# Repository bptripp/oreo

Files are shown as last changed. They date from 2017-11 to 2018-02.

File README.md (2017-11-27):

# oreo

OREO is a 7-degree-of-freedom robotic head that is modelled on the primate visual system. It performs saccades at realistic human speeds. The eyes have a realistic range of motion, including vergence. It also supports rapid changes in focus distance.

Further documentation is in development. In the mean time please contact Bryan Tripp (bptripp@uwaterloo.ca) for more information. 

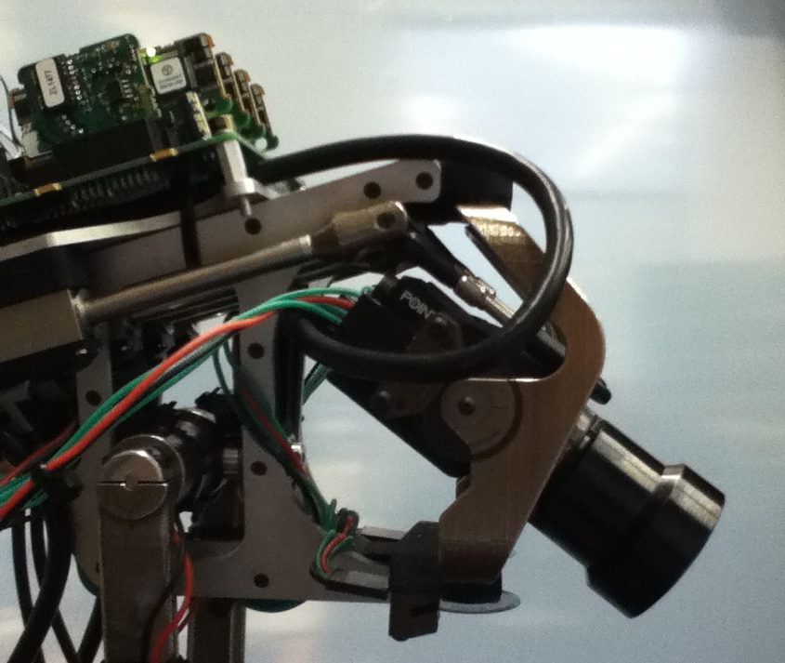
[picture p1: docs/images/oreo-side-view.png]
OREO photo


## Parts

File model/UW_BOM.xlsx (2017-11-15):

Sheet: Eye_Sub_ASM
PN | Description | Supplier | Material | Est. Cost (USD) 1 | Est. Cost (USD) 5 | Est. Cost (USD) 10 | QTY. / Package | QTY. Req'd | Order QTY. | Part Cost | CAD File name | Link
XXX | Lens Assembly | B-CON | Assembly | 0 | N/A | N/A | 1 | 1 | 1 | 0 | N/A | N/A
4262T5 | Ultra-Precision Mini Stainless Steel Ball Bearing - ABEC-7, Flanged Double Shielded for 3/32" Shaft Diameter, 5/16" OD | McMaster-Carr | 440C Stainless Steel | 12.76 | N/A | N/A | 1 | 3 | 3 | 38.28 | 4262T500.SLDPRT | http://www.mcmaster.com/#catalog/121/1183/=10p1i0g
90318A101 | Ultra Low Profile Type 316 Stainless Steel Shoulder Screw, Socket Drive, 3/32" Diameter X1/8" Long Shoulder, 2-56 Thread | McMaster-Carr | 316 Stainless Steel | 4.26 | 3.63 | N/A | 1 | 3 | 3 | 12.78 | 90318A101.SLDPRT | http://www.mcmaster.com/#90318a101/=10p1ko5
91294A002 | Class 10.9, M2 Size, 4mm Length, .4mm Pitch, Black Alloy Steel Flat-Head Socket Cap Screw | McMaster-Carr | Black-Oxide | 6.42 | N/A | N/A | 25 | 4 | 1 | 6.42 | 91294A002.SLDPRT | http://www.mcmaster.com/#91294a002/=10p1pz1
91239A758 | Class 10.9 Steel Button-Head Socket Cap Screw, M2.5 Size, 12 mm Length, .45 mm Pitch | McMaster-Carr | Black Oxide | 10.5 | N/A | N/A | 25 | 2 | 1 | 10.5 | 91239A758.SLDPRT | http://www.mcmaster.com/#91239a758/=10p1rd7
91255A075 | Alloy Steel Button-Head Socket Cap Screw, Black-Oxide, 2-56 Thread, 1/16" Long | McMaster-Carr | Black Oxide | 7.25 | N/A | N/A | 25 | 1 | 1 | 7.25 | 91255A075.SLDPRT | http://www.mcmaster.com/#91255a075/=10p1seu
9712K510 | High-Carbon Steel Belleville Disc Spring, .093" ID, .187" OD, .007" Thick | McMaster-Carr | High Carbon Steel | 12.03 | N/A | N/A | 12 | 1 | 1 | 12.03 | 9712K510.SLDPRT | http://www.mcmaster.com/#9712k51/=10p1tbr
99040A210 | Stainless Steel Shim for Shafts, 0.010" Thick, 0.093" ID, 0.203" OD | McMaster-Carr | 18-8 Stainless Steel | 11.29 | N/A | N/A | 25 | 2 | 1 | 11.29 | 99040A210.SLDPRT | http://www.mcmaster.com/#99040a210/=10p1zgw
91239A115 | Class 10.9 Steel Button-Head Socket Cap Screw, M3 Size, 10 mm Length, .5 mm Pitch | McMaster-Carr | Black Oxide | 6.88 | N/A | N/A | 100 | 2 | 1 | 6.88 | 91239A115.SLDPRT | http://www.mcmaster.com/#91239a115/=111uhff
FL3-U3-13S2M-CS | Camera, Flea3 | Point Grey | Assembly | 525 | N/A | N/A | 1 | 0 | 0 | 0 | FL2-006-R0.SLDPRT | https://www.ptgrey.com/flea3-13-mp-mono-usb3-vision-sony-imx035-camera
cam_mount_Al | Camera Mount Aluminum | ProtoLabs | 6061-T6 Aluminum | 468.14 | N/A | N/A | 1 | 0 | 0 | 0 | cam_mount.STEP | https://myaccount.protolabs.com
yoke_Al | Yoke Aluminum | ProtoLabs | 6061-T6 Aluminum | 1293.12 | N/A | N/A | 1 | 0 | 0 | 0 | yoke.STEP | https://myaccount.protolabs.com
cam_mount_SS | Camera Mount Stainless | Shapeways | Printed Stainless Steel | 48.14 | N/A | N/A | 1 | 0 | 0 | 0 | cam_mount.STL | https://www.shapeways.com
cam_mount_Ny | Camera Mount Plastic | Shapeways | Strong and Flexible Black | 13.46 | N/A | N/A | 1 | 0 | 0 | 0 | cam_mount.STL | https://www.shapeways.com
yoke_SS | Yoke Stainless | Shapeways | Printed Stainless Steel | 48.87 | N/A | N/A | 1 | 0 | 0 | 0 | yoke.STL | https://www.shapeways.com
yoke_Ny | Yoke Plastic | Shapeways | Strong and Flexible Black | 9.76 | N/A | N/A | 1 | 0 | 0 | 0 | yoke.STL | https://www.shapeways.com
EM2-1-5000-I | Encoder | US Digital | Plastic | 58.1 | 40.1 | 35.71 | 1 | 1 | 1 | 58.1 | EM1-X-X.SLDPRT | http://www.usdigital.com/products/encoders/incremental/modules/EM2
DISK-1-5000-093-IE | Encoder Disk | US Digital | Mylar | 13.63 | 9.42 | 8.11 | 1 | 2 | 2 | 27.26 | encoder_disk.SLDPRT | http://www.usdigital.com/products/encoders/incremental/rotary/disks/DISK-1
TOTAL |  |  |  |  |  |  |  |  |  | 190.79

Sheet: Frame_Sub_ASM
PN | Description | Supplier | Material | Est. Cost (USD) 1 | Est. Cost (USD) 5 | Est. Cost (USD) 10 | QTY. / Package | QTY. Req'd | Order QTY. | Part Cost | CAD File name | Link
B75AECFD27A3 | Motor | Maxon | Assembly | 318 | N/A | N/A | 1 | 1 | 1 | 318 | maxon_PN_B75AECFD27A3.sldasm | http://www.maxonmotorusa.com/maxon/view/configurator/?ConfigID=B75AECFD27A3
4262T5 | Ultra-Precision Mini Stainless Steel Ball Bearing - ABEC-7, Flanged Double Shielded for 3/32" Shaft Diameter, 5/16" OD | McMaster-Carr | 440C Stainless Steel | 12.76 | N/A | N/A | 1 | 4 | 4 | 51.04 | 4262T500.SLDPRT | http://www.mcmaster.com/#catalog/121/1183/=10p1i0g
90318A102 | Ultra Low Profile Type 316 Stainless Steel Shoulder Screw, Socket Drive, 3/32" Diameter X1/4" Long Shoulder, 2-56 Thread | McMaster-Carr | 316 Stainless Steel | 4.29 | 3.66 | N/A | 1 | 6 | 6 | 25.74 | 90318A102.SLDPRT | http://www.mcmaster.com/#90318a102/=10p2m1d
99040A210 | Stainless Steel Shim for Shafts, 0.010" Thick, 0.093" ID, 0.203" OD | McMaster-Carr | 18-8 Stainless Steel | 11.29 | N/A | N/A | 25 | 10 | 1 | 11.29 | 99040A210.SLDPRT | http://www.mcmaster.com/#99040a210/=10p1zgw
91239A758 | Class 10.9 Steel Button-Head Socket Cap Screw, M2.5 Size, 12 mm Length, .45 mm Pitch | McMaster-Carr | Black Oxide | 10.5 | N/A | N/A | 25 | 6 | 1 | 10.5 | 91239A758.SLDPRT | http://www.mcmaster.com/#91239a758/=10p1rd7
3088A119 | Steel Shim, Round, 0.001" Thick, 1/4" ID, 3/8" OD | McMaster-Carr | Steel | 5.22 | N/A | N/A | 10 | 4 | 1 | 5.22 | N/A | http://www.mcmaster.com/#3088a119/=10p39ua
3088A229 | Steel Shim, Round, 0.005" Thick, 1/4" ID, 3/8" OD | McMaster-Carr | Steel | 3.66 | N/A | N/A | 10 | 1 | 1 | 3.66 | N/A | http://www.mcmaster.com/#3088a229/=10p394m
4262T36 | Premium Flanged Ball Bearing, Double Shielded, Trade No.FR188-2Z | McMaster-Carr | 440C Stainless Steel | 10.47 | N/A | N/A | 1 | 3 | 3 | 31.41 | 4262T36.SLDPRT | http://www.mcmaster.com/#4262t36/=113ctkg
90337A197 | Low Profile 18-8 Stainless Steel Shoulder Screw, Socket Drive, 1/4" Diameter X5/8" Long Shoulder, 10-32 Thread | McMaster-Carr | 18-8 Stainless | 10.47 | 8.88 | N/A | 1 | 3 | 3 | 31.41 | 90337A197.SLDPRT | http://www.mcmaster.com/#90337a197/=10p3d4d
91294A005 | Black Alloy Steel Flat-Head Socket Cap Screw, Class 10.9, M2 Size, 8mm Length, .4mm Pitch | McMaster-Carr | Black Oxide | 6.45 | N/A | N/A | 25 | 30 | 2 | 12.9 | 91294A005.SLDPRT | http://www.mcmaster.com/#91294a005/=10p4dr9
91294A006 | Black Alloy Steel Flat-Head Socket Cap Screw, Class 10.9, M2 Size, 10mm Length, .4mm Pitch | McMaster-Carr | Black Oxide | 6.65 | N/A | N/A | 25 | 3 | 1 | 6.65 | 91294A006.SLDPRT | http://www.mcmaster.com/#91294a006/=10p4368
93657A005 | Metric Nylon Unthreaded Spacer 6mm OD, 4mm Length, M3 Screw Size | McMaster-Carr | Nylon | 1.06 | N/A | 0.89 | 1 | 8 | 8 | 8.48 | 93657A005.SLDPRT | http://www.mcmaster.com/#93657a005/=10qlcg0
91294A132 | Black Alloy Steel Flat-Head Socket Cap Screw, Class 10.9, M3 Size, 12mm Length, .50 Pitch | McMaster-Carr | Black Oxide | 5.38 | N/A | N/A | 100 | 4 | 1 | 5.38 | 91294A132.SLDPRT | http://www.mcmaster.com/#91294a132/=111u497
91292A265 | Type 18-8 Stainless Steel Socket Head Cap Screw, M1.6 Thread, 10mm Long, 0.35mm Pitch | McMaster-Carr | 18-8 Stainless | 9.78 | N/A | N/A | 50 | 16 | 1 | 9.78 | 91292A265.SLDPRT | http://www.mcmaster.com/#91292a265/=111u6c4
91239A115 | lass 10.9 Steel Button-Head Socket Cap Screw, M3 Size, 10 mm Length, .5 mm Pitc | McMaster-Carr | Black Oxide | 6.88 | N/A | N/A | 100 | 4 | 1 | 6.88 | 91239A115.SLDPRT | http://www.mcmaster.com/#91239a115/=111uhff
95893A550 | Thread-Forming Torx Screw for Plastics, Flat Head, 18-8 Stainless Steel, 2-28 Thread, 1/4" Length | McMaster-Carr | 18-8 Stainless | 12.24 | N/A | N/A | 50 | 30 | 1 | 12.24 | 95893A550.SLDPRT | http://www.mcmaster.com/#95893a550/=111u4qr
LM 1247–060–11 | Linear Actuator | MicroMo | Assembly | 539.3 | N/A | N/A | 1 | 6 | 6 | 3235.8 | LM1247-060-XX.SLDASM | http://www.micromo.com/products/linear-motors/quickshaft-data-sheets
Motor Mount Inside_AL | Motor Mount Inside | protolabs | 6061-T6 Aluminum | 291.5 | N/A | N/A | 1 | 0 | 0 | 0 | motor_mount_inside.STEP | https://myaccount.protolabs.com
Yaw Bottom Bearing Mount_AL | Yaw Bottom Bearing Mount | protolabs | 6061-T6 Aluminum | 187.81 | N/A | N/A | 1 | 0 | 0 | 0 | yaw_bearing_mount_bottom.STEP | https://myaccount.protolabs.com
Yaw Top Bearing Mount_AL | Yaw Top Bearing Mount | protolabs | 6061-T6 Aluminum | 175.12 | N/A | N/A | 1 | 0 | 0 | 0 | yaw_bearing_mount_top.STEP | https://myaccount.protolabs.com
Roll Motor Mount_AL | Roll Motor Mount | protolabs | 6061-T6 Aluminum | 189.09 | N/A | N/A | 1 | 0 | 0 | 0 | roll_motor_mount.STEP | https://myaccount.protolabs.com
Roll Bearing Mount_AL | Roll Bearing Mount | protolabs | 6061-T6 Aluminum | 429.5 | N/A | N/A | 1 | 0 | 0 | 0 | roll_bearing_mount.STEP | https://myaccount.protolabs.com
frame_plate_side_l | frame_plate_side_l | ProtoLabs | 7075-T651 Aluminum | 150.04 | 123.13 | 111.41 | 1 | 1 | 1 | 150.04 | frame_plate_side_l.STEP | https://myaccount.protolabs.com
frame_plate_side_r | frame_plate_side_r | ProtoLabs | 7075-T651 Aluminum | 150.04 | 123.13 | 111.41 | 1 | 1 | 1 | 150.04 | frame_plate_side_r.STEP | https://myaccount.protolabs.com
frame_plate_top | frame_plate_top | ProtoLabs | 7075-T651 Aluminum | 160.02 | 133.1 | 121.38 | 1 | 1 | 1 | 160.02 | frame_plate_top.STEP | https://myaccount.protolabs.com
Motor Mount Inside_SS | Motor Mount Inside | Shapeways | Printed Stainless Steel | 51.92 | N/A | N/A | 1 | 0 | 0 | 0 | motor_mount_inside.STL | https://www.shapeways.com
Motor Mount Inside_NY | Motor Mount Inside | Shapeways | Strong and Flexible Black | 8.88 | N/A | N/A | 1 | 0 | 0 | 0 | motor_mount_inside.STL | https://www.shapeways.com
Yaw Bottom Bearing Mount_SS | Yaw Bottom Bearing Mount | Shapeways | Printed Stainless Steel | 73.84 | N/A | N/A | 1 | 0 | 0 | 0 | yaw_bearing_mount_bottom.STL | https://www.shapeways.com
Yaw Bottom Bearing Mount_NY | Yaw Bottom Bearing Mount | Shapeways | Strong and Flexible Black | 11.06 | N/A | N/A | 1 | 0 | 0 | 0 | yaw_bearing_mount_bottom.STL | https://www.shapeways.com
Yaw Top Bearing Mount_SS | Yaw Top Bearing Mount | Shapeways | Printed Stainless Steel | 87.83 | N/A | N/A | 1 | 0 | 0 | 0 | yaw_bearing_mount_top.STL | https://www.shapeways.com
Yaw Top Bearing Mount_NY | Yaw Top Bearing Mount | Shapeways | Strong and Flexible Black | 13.25 | N/A | N/A | 1 | 0 | 0 | 0 | yaw_bearing_mount_top.STL | https://www.shapeways.com
Roll Motor Mount_SS | Roll Motor Mount | Shapeways | Printed Stainless Steel | 89.08 | N/A | N/A | 1 | 0 | 0 | 0 | roll_motor_mount.STL | https://www.shapeways.com
Roll Motor Mount_NY | Roll Motor Mount | Shapeways | Strong and Flexible Black | 13.66 | N/A | N/A | 1 | 0 | 0 | 0 | roll_motor_mount.STL | https://www.shapeways.com
Roll Bearing Mount_SS | Roll Bearing Mount | Shapeways | Printed Stainless Steel | 123.93 | N/A | N/A | 1 | 0 | 0 | 0 | roll_bearing_mount.STL | https://www.shapeways.com
Roll Bearing Mount_NY | Roll Bearing Mount | Shapeways | Strong and Flexible Black | 17.39 | N/A | N/A | 1 | 0 | 0 | 0 | roll_bearing_mount.STL | https://www.shapeways.com
Dogbone Link_NY | Dogbone Link | Shapeways | Strong and Flexible Black | 3.37 | N/A | N/A | 1 | 0 | 0 | 0 | dogbone_link.STL | https://www.shapeways.com
Dogbone Link_SS | Dogbone Link | Shapeways | Stainless Steel | 11.16 | N/A | N/A | 1 | 0 | 0 | 0 | dogbone_link.STL | https://www.shapeways.com
LM1247 Spacer_NY | LM1247 Spacer | Shapeways | Strong and Flexible Black | 5.86 | N/A | N/A | 1 | 0 | 0 | 0 | lm1247_spacer.STL | https://www.shapeways.com
LM1247 Spacer_SS | LM1247 Spacer | Shapeways | Stainless Steel | 25.9 | N/A | N/A | 1 | 0 | 0 | 0 | lm1247_spacer.STL | https://www.shapeways.com
P028.002.E894 | iPOS360x SX Multi-axis Motion System | Technosoft Motion | iPOS360x MBX-NET | 200 | ~ |  | 1 | 1 | 1 | 200 | iPOS360xMulti.SLDPRT | http://www.technosoftmotion.com/en/intelligent-drives-and-motors/ipos-line/ipos-multi-axis/ipos360x-sx
P028.001.E001 | iPOS3602 VX Intelligent Drive (75 W, CANopen / EtherCAT) | Technosoft Motion | iPOS3602 VX-CAN | 300 | ~ |  | 1 | 6 | 6 | 1800 | iPOS360xMulti.SLDPRT | http://www.technosoftmotion.com/en/intelligent-drives-and-motors/ipos-line/ipos3602/ipos3602-vx
P038.022.E001 | Ethernet-CAN Adapter | Technosoft Motion | ENET-VX Ethernet plug-in interface | 75 | not sure of this price |  | 1 | 1 | 1 | 75 | iPOS360xMulti.SLDPRT | http://www.technosoftmotion.com/en/starter-kits-and-accessories/ethernet-can-adapter#description
EM2-1-5000-I | Encoder | US Digital | Mylar | 58.1 | 40.1 | 35.71 | 1 | 3 | 3 | 174.3 | EM1-X-X.SLDPRT | http://www.usdigital.com/products/encoders/incremental/modules/EM2
DISK-1-5000-093-IE | Encoder Disk | US Digital | Mylar | 13.63 | 9.42 | 8.11 | 1 | 2 | 2 | 27.26 | encoder_disk.SLDPRT | http://www.usdigital.com/products/encoders/incremental/rotary/disks/DISK-1
HUBDISK-1-5000-250-IE | Encoder Disk, 5000 CPR, Index, 1/4" Hub | US Digital | Mylar | 20.53 | 14.16 | 10.81 | 1 | 1 | 1 | 20.53 | HUBDISK-1-5000-250-IE.SLDPRT | http://www.usdigital.com/products/encoders/incremental/rotary/disks/HUBDISK-1
TOTAL |  |  |  |  |  |  |  |  |  | 6543.57

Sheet: Neck_Sub_ASM
PN | Description | Supplier | Material | Est. Cost (USD) 1 | Est. Cost (USD) 5 | Est. Cost (USD) 10 | QTY. / Package | QTY. Req'd | Order QTY. | Part Cost | CAD File name | Link
B75AECFD27A3 | Motor | Maxon | Assembly | 318 | N/A | N/A | 1 | 2 | 2 | 636 | maxon_PN_B75AECFD27A3.sldasm | http://www.maxonmotorusa.com/maxon/view/configurator/?ConfigID=B75AECFD27A3
91239A758 | Class 10.9 Steel Button-Head Socket Cap Screw, M2.5 Size, 12 mm Length, .45 mm Pitch | McMaster-Carr | Black Oxide | 10.5 | N/A | N/A | 25 | 10 | 1 | 10.5 | 91239A758.SLDPRT | http://www.mcmaster.com/#91239a758/=10p1rd7
4262T36 | Premium Flanged Ball Bearing, Double Shielded, Trade No.FR188-2Z | McMaster-Carr | 440C Stainless Steel | 10.47 | N/A | N/A | 1 | 3 | 3 | 31.41 | 4262T36.SLDPRT | http://www.mcmaster.com/#4262t36/=113ctkg
90337A197 | Low Profile 18-8 Stainless Steel Shoulder Screw, Socket Drive, 1/4" Diameter X5/8" Long Shoulder, 10-32 Thread | McMaster-Carr | 18-8 Stainless | 10.47 | 8.88 | N/A | 1 | 2 | 2 | 20.94 | 90337A197.SLDPRT | http://www.mcmaster.com/#90337a197/=10p3d4d
9520T270 | Two-Piece Clamp-on Shaft Collar for 3 mm Diameter, Aluminum | McMaster-Carr | Aluminum | 7.71 | N/A | N/A | 1 | 1 | 1 | 7.71 | 9520T270.SLDPRT | http://www.mcmaster.com/#9520t27/=10p5h4m
91385A201 | Thread-Locking Cup Point Set Screw, Alloy Steel, M2 Size, 3mm Long, 0.4mm Pitch | McMaster-Carr | Black Oxide | 12.23 | N/A | N/A | 10 | 2 | 1 | 12.23 | 91385A201.SLDPRT | http://www.mcmaster.com/#91385a201/=10p5ipp
91294A003 | Black Alloy Steel Flat-Head Socket Cap Screw, Class 10.9, M2 Size, 5mm Length, .4mm Pitch | McMaster-Carr | Black Oxide | 6.24 | N/A | N/A | 25 | 12 | 1 | 6.24 | 91294A003.SLDPRT | http://www.mcmaster.com/#91294a003/=10p5k73
6680K11 | Dual-Load Angular-Contact Steel Ball Bearing, Open, 10mm Shaft Diameter, 30mm Outside Diamete | McMaster-Carr | 52100 Steel | 30.09 | N/A | N/A | 1 | 2 | 2 | 60.18 | 6680K110.SLDPRT | http://www.mcmaster.com/#6680k11/=10qk24x
3088A124 | Steel Shim Round, 0.001" Thick, 3/4" ID, 1-1/8" OD | McMaster-Carr | 1008-1010 Steel | 6.36 | N/A | N/A | 10 | 1 | 1 | 6.36 | 3088A124.SLDPRT | http://www.mcmaster.com/#3088a124/=10qk6ci
94805A217 | 3/8"-24 Thread Size, 9/16" Wide, 7/32" High, Thin Hex Nut | McMaster-Carr | 316 Stainless Steel | 7.62 | N/A | N/A | 25 | 1 | 1 | 7.62 | 94805A217.SLDPRT | http://www.mcmaster.com/#94805a217/=10qk7p0
97648A420 | Press-in Nut for Sheet Metal M4 X 0.7 Thread Size | McMaster-Carr | 18-8 Stainless | 8.15 | N/A | N/A | 10 | 4 | 1 | 8.15 | 97648A420.SLDPRT | http://www.mcmaster.com/#97648a420/=10qlboa
93657A005 | Metric Nylon Unthreaded Spacer 6mm OD, 4mm Length, M3 Screw Size | McMaster-Carr | Nylon | 1.06 | N/A | 0.89 | 1 | 4 | 4 | 4.24 | 93657A005.SLDPRT | http://www.mcmaster.com/#93657a005/=10qlcg0
91239A144 | Class 10.9 STL Button-Head Socket Cap Screw M4 Size, 10 mm Length, .7 mm Pitch | McMaster-Carr | Black Oxide | 9.47 | N/A | N/A | 100 | 11 | 1 | 9.47 | 91239A144.SLDPRT | http://www.mcmaster.com/#91239a144/=10qld2f
94150A325 | Type 316 Stainless Steel Hex Nut M3X0.5 Thread Size, 5.5mm Wide, 2.4mm High | McMaster-Carr | 316 Stainless Steel | 3.08 | N/A | N/A | 50 | 4 | 1 | 3.08 | 94150A325.SLDPRT | http://www.mcmaster.com/#94150a325/=10qle1w
91294A134 | Flat-Head Socket Cap Screw Class 10.9, M3 Size, 16mm Length, .50mm Pitch | McMaster-Carr | Black Oxide | 7.95 | N/A | N/A | 100 | 4 | 1 | 7.95 | 91294A134.SLDPRT | http://www.mcmaster.com/#91294a134/=10qleyx
motor_mount_AL | motor_mount | protolabs | 6061-T6 Aluminum | 212.21 | N/A | N/A | 1 | 0 | 0 | 0 | motor_mount.STEP | https://myaccount.protolabs.com
pitch_body_AL | pitch_body | protolabs | 6061-T6 Aluminum | 270.15 | N/A | N/A | 1 | 0 | 0 | 0 | pitch_body.STEP | https://myaccount.protolabs.com
pitch_stop_AL | pitch_stop | protolabs | 6061-T6 Aluminum | 88.96 | N/A | N/A | 1 | 0 | 0 | 0 | pitch_stop.STEP | https://myaccount.protolabs.com
yaw_link_AL | yaw_link | protolabs | 6061-T6 Aluminum | 692.82 | N/A | N/A | 1 | 0 | 0 | 0 | yaw_link.STEP | https://myaccount.protolabs.com
yaw_shaft_AL | yaw_shaft | protolabs | 7075 Aluminum | 105.46 | N/A | N/A | 1 | 0 | 0 | 0 | yaw_shaft.STEP | https://myaccount.protolabs.com
motor_mount_SS |  | Shapeways | Printed Stainless Steel | 181.52 | N/A | N/A | 1 | 0 | 0 | 0 | motor_mount.STL | https://www.shapeways.com
motor_mount_NY |  | Shapeways | Strong and Flexible Black | 25.8 | N/A | N/A | 1 | 0 | 0 | 0 | motor_mount.STL | https://www.shapeways.com
pitch_body_SS |  | Shapeways | Printed Stainless Steel | 72.99 | N/A | N/A | 1 | 0 | 0 | 0 | pitch_body.STL | https://www.shapeways.com
pitch_body_NY |  | Shapeways | Strong and Flexible Black | 13.54 | N/A | N/A | 1 | 0 | 0 | 0 | pitch_body.STL | https://www.shapeways.com
pitch_stop_SS |  | Shapeways | Printed Stainless Steel | 12.88 | N/A | N/A | 1 | 0 | 0 | 0 | pitch_stop.STL | https://www.shapeways.com
pitch_stop_NY |  | Shapeways | Strong and Flexible Black | 3.41 | N/A | N/A | 1 | 0 | 0 | 0 | pitch_stop.STL | https://www.shapeways.com
yaw_link_SS |  | Shapeways | Printed Stainless Steel | 210.86 | N/A | N/A | 1 | 0 | 0 | 0 | yaw_link.STL | https://www.shapeways.com
yaw_link_NY |  | Shapeways | Strong and Flexible Black | 26.37 | N/A | N/A | 1 | 0 | 0 | 0 | yaw_link.STL | https://www.shapeways.com
yaw_shaft_SS |  | Shapeways | Printed Stainless Steel | 31.72 | N/A | N/A | 1 | 0 | 0 | 0 | yaw_shaft.STL | https://www.shapeways.com
yaw_shaft_NY |  | Shapeways | Strong and Flexible Black | 5.85 | N/A | N/A | 1 | 0 | 0 | 0 | yaw_shaft.STL | https://www.shapeways.com
P028.002.E894 | iPOS360x SX Multi-axis Motion System | Technosoft Motion | iPOS360x MBX-NET rev C | 200 | ~ |  | 1 | 1 | 1 | 200 | iPOS360xMulti.SLDPRT | http://www.technosoftmotion.com/en/intelligent-drives-and-motors/ipos-line/ipos-multi-axis/ipos360x-sx
P028.001.E001 | iPOS3602 VX Intelligent Drive (75 W, CANopen / EtherCAT) | Technosoft Motion | iPOS3602 VX-CAN | 300 | ~ |  | 1 | 3 | 3 | 900 | iPOS360xMulti.SLDPRT | http://www.technosoftmotion.com/en/intelligent-drives-and-motors/ipos-line/ipos3602/ipos3602-vx
P038.022.E001 | Ethernet-CAN Adapter | Technosoft Motion | ENET-VX Ethernet plug-in interface | 75 | not sure of this price |  | 1 | 1 | 1 | 75 | iPOS360xMulti.SLDPRT | http://www.technosoftmotion.com/en/starter-kits-and-accessories/ethernet-can-adapter#description
EM2-1-5000-I | Encoder | US Digital | Mylar | 58.1 | 40.1 | 35.71 | 1 | 3 | 3 | 174.3 | EM1-X-X.SLDPRT | http://www.usdigital.com/products/encoders/incremental/modules/EM2
HUBDISK-1-5000-250-IE | Encoder Disk, 5000 CPR, Index, 1/4" Hub | US Digital | Mylar | 20.53 | 14.16 | 10.81 | 1 | 2 | 2 | 41.06 | HUBDISK-1-5000-250-IE.SLDPRT | http://www.usdigital.com/products/encoders/incremental/rotary/disks/HUBDISK-1
HUBDISK-1-5000-313-IE | Encoder Disk, 5000 CPR, Index, 5/16" Hub | US Digital | Mylar | 20.53 | 14.16 | 10.81 | 1 | 1 | 1 | 20.53 | HUBDISK-1-5000-313-IE.SLDPRT | http://www.usdigital.com/products/encoders/incremental/rotary/disks/DISK-1
TOTAL |  |  |  |  |  |  |  |  |  | 2242.97
Parts to add
Neck Base
Vesa Mount

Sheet: Dogbone_ASM
PN | Description | Supplier | Material | Est. Cost (USD) 1 | Est. Cost (USD) 5 | Est. Cost (USD) 10 | QTY. / Package | QTY. Req'd | Order QTY. | Part Cost | CAD File name | Link
017000318-0 | Ball Joint Spacers | Hobby King | Brass | 0.8 | N/A | N/A | 10 | 16 | 2 | 1.6 | N/A | http://www.hobbyking.com/hobbyking/store/__43259__Ball_Joint_Spacers_2mm_10pc.html
OR023-00501 | Ball and roller link 4.8x2x18mm (10pcs/set) | Hobby King | Brass | 3.82 | N/A | N/A | 10 | 8 | 1 | 3.82 | N/A | http://www.hobbyking.com/hobbyking/store/__8855__Ball_and_roller_link_4_8x2x18mm_10pcs_set_.html
T1330A | Curved Ball Link Pliers 5mm | Hobby King | Tool | 6.9 | N/A | N/A | 1 | 1 | 1 | 6.9 | N/A | http://www.hobbyking.com/hobbyking/store/__9801__Curved_Ball_Link_Pliers_5mm.html
450000351-0 | M2x45mm Stainless Steel Push Rods (LH & RH Threaded) (10pcs) | Hobby King | Stainless Steel | 3.36 | N/A | N/A | 10 | 4 | 1 | 3.36 | N/A | http://www.hobbyking.com/hobbyking/store/__61886__M2x45mm_Stainless_Steel_Push_Rods_LH_RH_Threaded_10pcs_.html
450000352-0 | M2x55mm Stainless Steel Push Rods (LH & RH Threaded) (10pcs) | Hobby King | Stainless Steel | 3.99 | N/A | N/A | 10 | 4 | 1 | 3.99 | N/A | http://www.hobbyking.com/hobbyking/store/__61887__M2x55mm_Stainless_Steel_Push_Rods_LH_RH_Threaded_10pcs_.html
RJX23 | M3 Steel Linkage Ball for all helis (10pcs) | Hobby King | Steel | 3.49 | N/A | N/A | 10 | 8 | 1 | 3.49 | N/A | http://www.hobbyking.com/hobbyking/store/__12301__M3_Steel_Linkage_Ball_for_all_helis_10pcs_.html
388000043 | 4.8mm x 15mm Ball End | Hobby King | Plastic | 1.93 | N/A | N/A | 10 | 4 | 1 | 1.93 | N/A | http://www.hobbyking.com/hobbyking/store/__26699__4_8mm_x_15mm_Ball_End_Turnigy_TD10_4WD_Touring_Car_10pc_.html
V2_5090-1612 | TZ-V2 .50 & .90 Size Ball Link | Hobby King | Plastic | 2.32 | N/A | N/A | 10 | 4 | 1 | 2.32 | N/A | http://www.hobbyking.com/hobbyking/store/__10524__TZ_V2_50_90_Size_Ball_Link.html
17000198-0 | M3 x 45mm Steel Push Rod (10pc) | Hobby King | Steel | 2.91 | N/A | N/A | 10 | 4 | 1 | 2.91 | N/A | http://www.hobbyking.com/hobbyking/store/RC_PRODUCT_SEARCH.asp?searchType=10&strSearch=Ball&location=HK&idCategory=&sortBy=Relevant&NumPerPage=20&currentPage=15
E4005 | E4005 Servo Ball Head Pack for Firefox (4pcs/set) | Hobby King | Steel | 1.49 | N/A | N/A | 4 | 4 | 1 | 1.49 | N/A | http://www.hobbyking.com/hobbyking/store/__9248__E4005_Servo_Ball_Head_Pack_for_Firefox_4pcs_set_.html
110BS-30810 | Ball Stud (M2*S Dia4)(10Pcs/Bag) - 110BS, 118B, A2023T, A2027, A2028, A2029, A2035, A2040 and A3011 | Hobby King | Steel | 2.09 | N/A | N/A | 10 | 4 | 1 | 2.09 | N/A | http://www.hobbyking.com/hobbyking/store/__14138__Ball_Stud_M2_S_Dia4_10Pcs_Bag_110BS_118B_A2023T_A2027_A2028_A2029_A2035_A2040_and_A3011.html
TOTAL |  |  |  |  |  |  |  |  |  | 33.9
dogbone link
Other Possible Vendors
http://www.traxxas.com
http://shop.dubro.com/c/aircraft_ball-links
http://www.helidirect.com
http://www3.towerhobbies.com
http://www.helidirect.com

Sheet: Cables&Connectors
PN | Description | Supplier | Material | Est. Cost (USD) 1 | Est. Cost (USD) 5 | Est. Cost (USD) 10 | QTY. / Package | QTY. Req'd | Order QTY. | Part Cost | CAD File name | Link
69845K62 | Steel Adhesive Back Cable Holder, Flexible Strap, for 5/16" Bundle Diameter, packs of 25 | McMaster-Carr | Steel | 12.63 | N/A | N/A | 25 | 25 | 1 | 12.63 | N/A | http://www.mcmaster.com/#69845k62/=1121qc3
1810A27 | Loctite® 222 Threadlocker, 0.34 oz. Bottle | McMaster-Carr | Loctite Purple | 13.65 | N/A | N/A | 1 | 1 | 1 | 13.65 | N/A | http://www.mcmaster.com/#1810a27/=113d0tu
653-A22E-M-02 | Pushbutton Switches DPST-NC 40mm HEAD Push-lock turn-reset | Mouser | Assembly | 44.44 | N/A | 42.43 | 1 | 1 | 1 | 44.44 | N/A | http://www.mouser.com/Search/ProductDetail.aspx?R=A22E-M-02virtualkey65350000virtualkey653-A22E-M-02
565-6733-0 | Hook-up Wire SILICONE LD BLK 50' | Mouser | Silicone | 25.99 | N/A | 24.93 | 50 | 10 | 1 | 25.99 | N/A | http://www.mouser.com/Search/ProductDetail.aspx?R=6733-0virtualkey56520000virtualkey565-6733-0
571-5-103976-4 | Headers & Wire Housings HSG&REC 1X05C STD 28-22 AWG | Mouser | Assembly | 1.63 | N/A | N/A | 1 | 10 | 10 | 16.3 | N/A | http://www.mouser.com/Search/ProductDetail.aspx
108-PMT-24V350W1AK | Switching Power Supplies 24V 350W Enclosed FrontFace PanelMt. | Mouser | Assembly | 56.95 | 55.22 | 53.5 | 1 | 1 | 1 | 56.95 | N/A | http://www.mouser.com/Search/ProductDetail.aspx
538-43030-0001-CT | Headers & Wire Housings MF 3.0 TERM 20-24G F Cut Strip of 100 | Mouser | Phosphor Bronze | 6.9 | N/A | N/A | 100 | 58 | 1 | 6.9 | N/A | http://www.mouser.com/Search/ProductDetail.aspx
538-50394-8051-CT | Headers & Wire Housings CRMP TERM 22-26G F Cut Strip of 100 | Mouser | Phosphor Bronze | 8.3 | N/A | N/A | 100 | 32 | 1 | 8.3 | N/A | http://www.mouser.com/Search/ProductDetail.aspx
538-43025-0400 | Headers & Wire Housings RECEPTACLE 4P DUAL ROW | Mouser | Polyester | 0.39 | N/A | 0.38 | 1 | 6 | 6 | 2.34 | N/A | http://www.mouser.com/Search/ProductDetail.aspx
538-43025-1400 | Headers & Wire Housings RECEPTACLE 14P DUAL ROW | Mouser | Polyester | 0.91 | N/A | 0.721 | 1 | 10 | 10 | 9.1 | N/A | http://www.mouser.com/Search/ProductDetail.aspx
538-43025-1000 | Headers & Wire Housings RECEPTACLE 10P DUAL ROW | Mouser | Polyester | 0.62 | N/A | 0.575 | 1 | 12 | 12 | 7.44 | N/A | http://www.mouser.com/Search/ProductDetail.aspx
538-51110-1056 | Headers & Wire Housings 10CKT 2MM MGRID WTB CONN CRIMP | Mouser | Polyester | 0.27 | N/A | 0.264 | 1 | 10 | 10 | 2.7 | N/A | http://www.mouser.com/Search/ProductDetail.aspx
571-3828118 | Headers & Wire Housings ECONOMY SHUNT ASSY | Mouser | Polyester | 0.1 | N/A | 0.088 | 1 | 10 | 10 | 1 | N/A | http://www.mouser.com/Search/ProductDetail.aspx?R=382811-8virtualkey57100000virtualkey571-3828118
574-W28-6H | Hook-up Wire 28 AWG BLK 100 FT | Mouser | Tefzel | 30.86 | N/A | 28.22 | 100 | 35 | 1 | 30.86 | N/A | http://www.mouser.com/Search/ProductDetail.aspx?R=W28-6Hvirtualkey57400000virtualkey574-W28-6H
644-HSTT12-48-TL | Heat Shrink Tubing and Sleeves H/S Thin .12" Dia Black | Mouser | PO | 1.22 | N/A | 1.16 | 1 | 1 | 1 | 1.22 | N/A | http://www.mouser.com/Search/ProductDetail.aspx
644-HSTTV25-48-Q | Heat Shrink Tubing and Sleeves 48" X 1/4" BLACK | Mouser | PO | 5.28 | 4.69 | 4.09 | 1 | 1 | 1 | 5.28 | N/A | http://www.mouser.com/Search/ProductDetail.aspx
644-HSTTV19-48-Q | Heat Shrink Tubing and Sleeves HeatShrink Thin VW-1 .19"(4.8mm) Dia | Mouser | PO | 2.04 | N/A | N/A | 1 | 1 | 1 | 2.04 | N/A | http://www.mouser.com/Search/ProductDetail.aspx
644-HSTTV06-48-Q | Heat Shrink Tubing and Sleeves H/S Thin VW-1 .06 "(1.6mm) Dia | Mouser | PO | 1.2 | N/A | 1.14 | 1 | 1 | 1 | 1.2 | N/A | http://www.mouser.com/Search/ProductDetail.aspx
US2-AMCBR2I1.5 | USB 3.0 A to Right Angle-2 Micro B with Locking Cable - Black (1.5 m) | ntc distributing |  | 27 | N/A | 26 | 1 | 2 | 2 | 54 | N/A | http://www.ntcdistributing.com/usb-3-0-a-to-right-angle-2-micro-b-with-locking-cable-black-1-5-m/
US2-AMCBR4I1-1.5 | USB 3.0 A to Right Angle-4 Micro B with Lock Cable - Black (1.5 m) | ntc distributing |  | 27 | N/A | 26 | 1 | 2 | 2 | 54 | N/A | http://www.ntcdistributing.com/usb-3-0-a-to-right-angle-4-micro-b-with-lock-cable-black-1-5-m/
TOTAL |  |  |  |  |  |  |  |  |  | 356.34
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

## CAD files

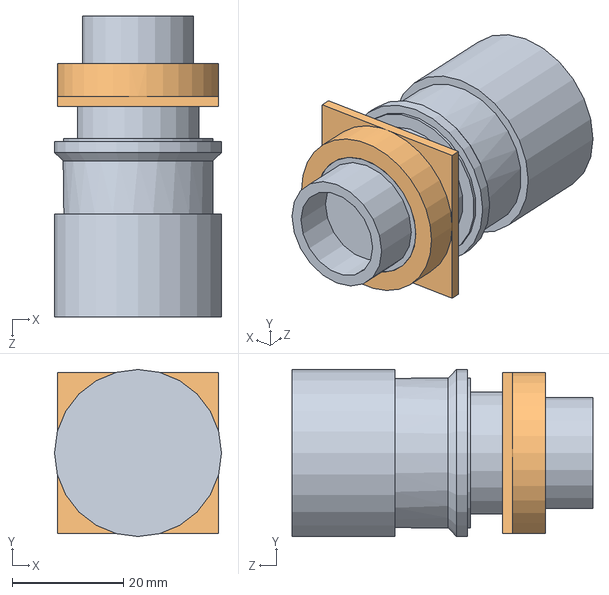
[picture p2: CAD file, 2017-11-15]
model/estop/A22E_S.SLDASM
30.0 x 30.0 x 54.0 mm
A22E_S_BASE
A22E_S_NUTS

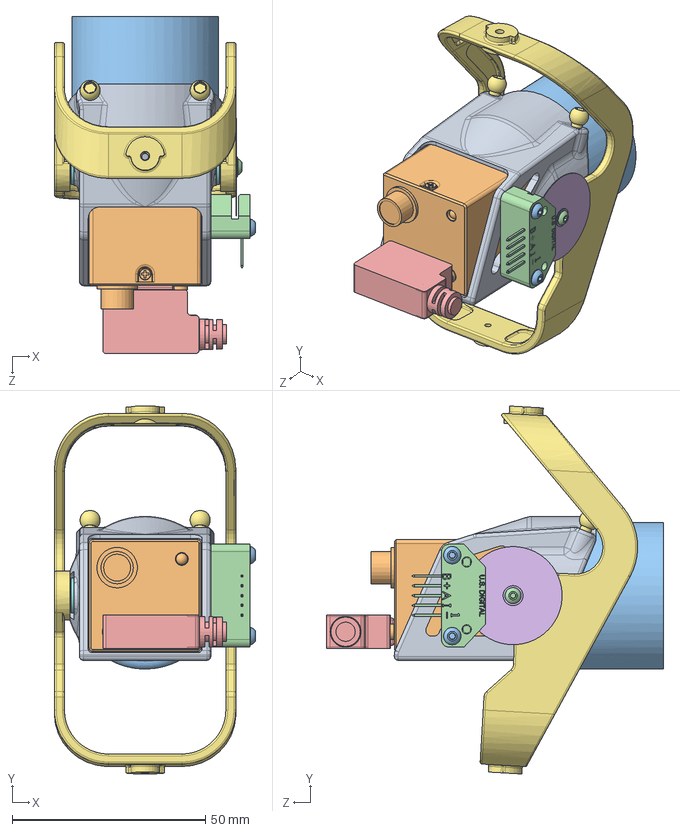
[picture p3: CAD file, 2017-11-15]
model/eye_sub_asm.SLDASM
52.1 x 95.3 x 87.4 mm
cam_mount
FL2-006-R0
lens
EM1-X-X
USBFIREWIRE_COM-MCBR3
encoder_disk
yoke
4262T500 x 2
90318A101 x 2
91294A002 x 4
91239A758 x 2
91255A075
9712K510
99040A210 x 2

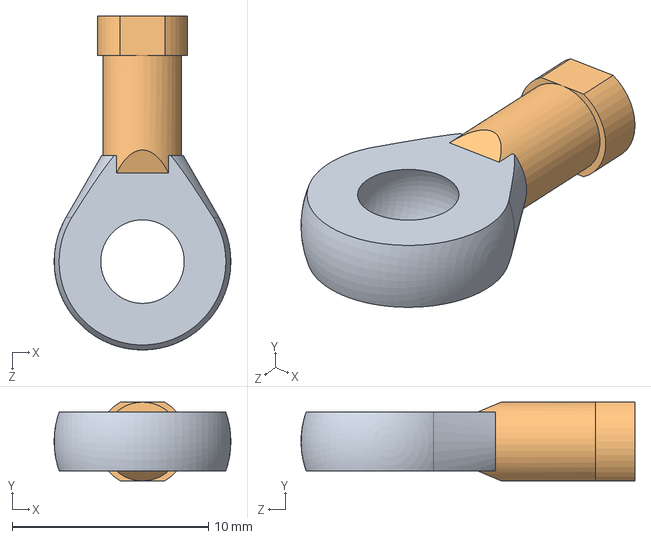
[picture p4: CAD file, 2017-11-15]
model/KBRM_02_1.SLDASM
9.00 x 4.00 x 17.0 mm

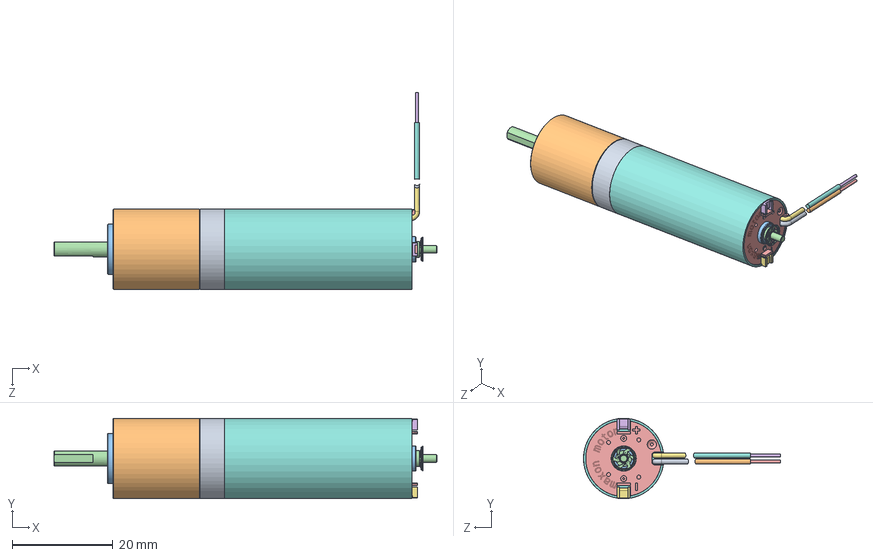
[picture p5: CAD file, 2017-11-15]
model/maxon16dxl/maxon_PN_B75AECFD27A3.sldasm
76.2 x 16.0 x 39.2 mm
maxon_PN_B75AECFD27A3_1
maxon_PN_B75AECFD27A3_2
maxon_PN_B75AECFD27A3_3
maxon_PN_B75AECFD27A3_3_2
maxon_PN_B75AECFD27A3_4
maxon_PN_B75AECFD27A3_4_2
maxon_PN_B75AECFD27A3_5
maxon_PN_B75AECFD27A3_5_2
maxon_PN_B75AECFD27A3_6
maxon_PN_B75AECFD27A3_6_2
maxon_PN_B75AECFD27A3_7
maxon_PN_B75AECFD27A3_7_2
maxon_PN_B75AECFD27A3_8
maxon_PN_B75AECFD27A3_8_2
maxon_PN_B75AECFD27A3_8_3
maxon_PN_B75AECFD27A3

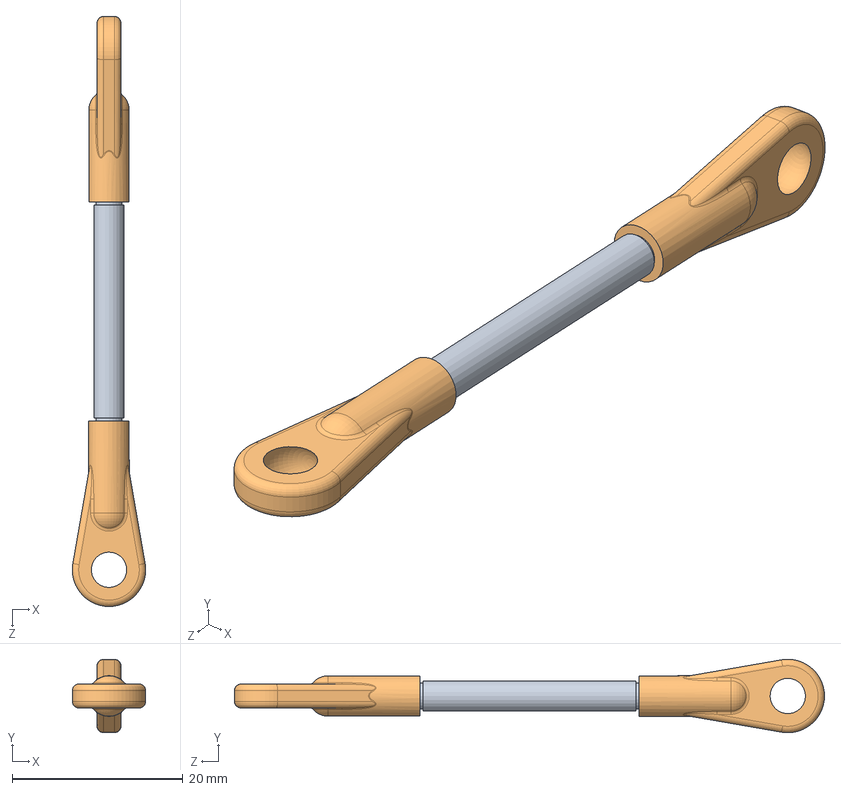
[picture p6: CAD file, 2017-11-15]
model/dogbone.SLDASM
8.59 x 8.59 x 69.1 mm
pushrod
rod_end_2 x 2

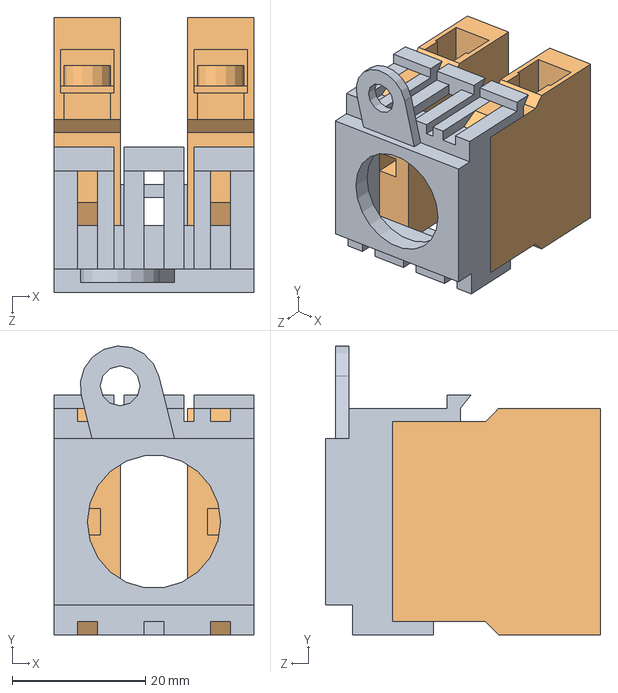
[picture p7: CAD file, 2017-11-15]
model/estop/A22_01M.SLDASM
30.0 x 43.4 x 41.2 mm
A22_3200
A22_01 x 2

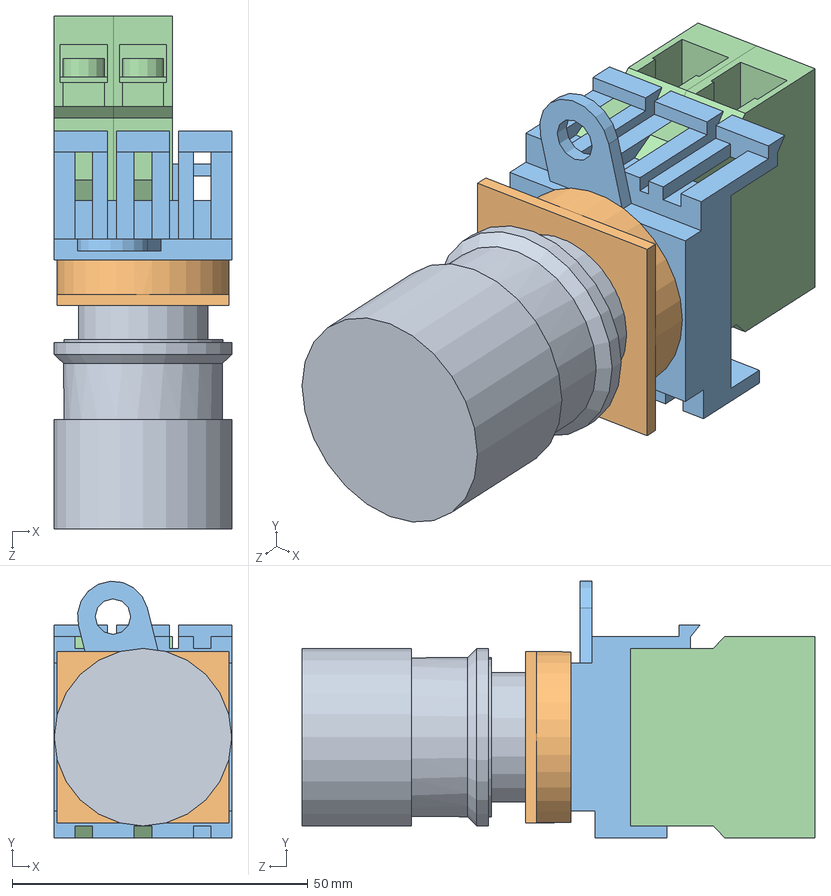
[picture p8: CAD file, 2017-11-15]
model/estop/A22E_S_02.SLDASM
30.0 x 43.4 x 86.7 mm
A22E_S_BASE
A22E_S_NUTS
A22_3200
A22_01 x 2

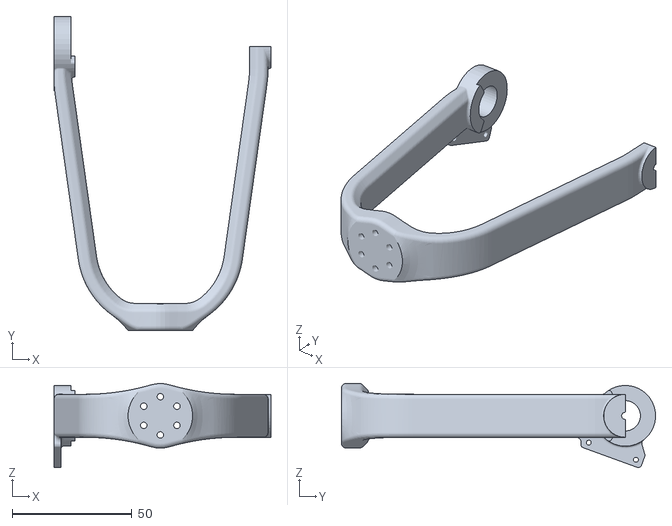
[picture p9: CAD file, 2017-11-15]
model/2016_07_13_MFG_RELEASE/yaw_link.STL
90.7 x 131.3 x 35.1

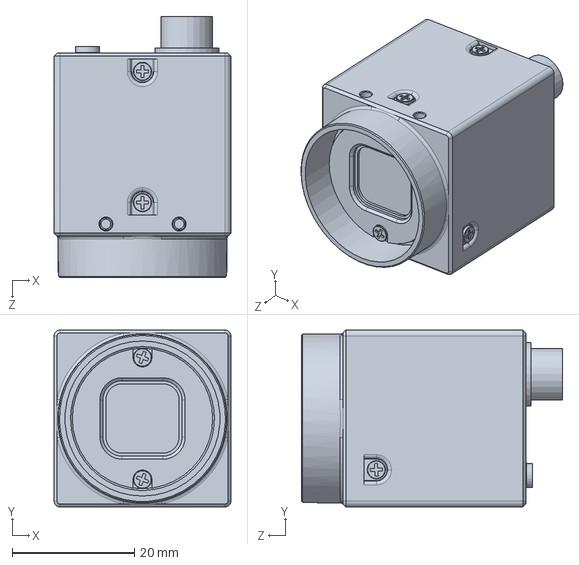
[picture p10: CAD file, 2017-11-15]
model/FL3_U3_Dimensions/FL3_U3-CSMount/FL2-006-R0.SLDPRT
29.0 x 29.0 x 42.8 mm

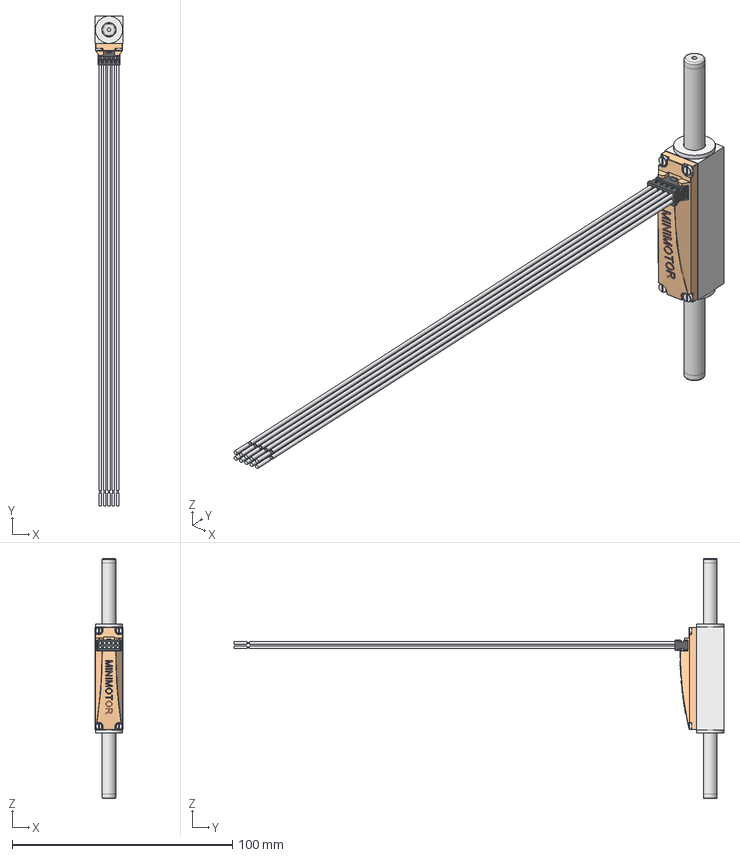
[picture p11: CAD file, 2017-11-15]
model/LM_1247/LM1247-040-XX.stp
12.5 x 222.3 x 109.0 mm
LM1247_xxx_xx_Housing
LM1247_040_Rod
LM1247_Wires_&_Connector

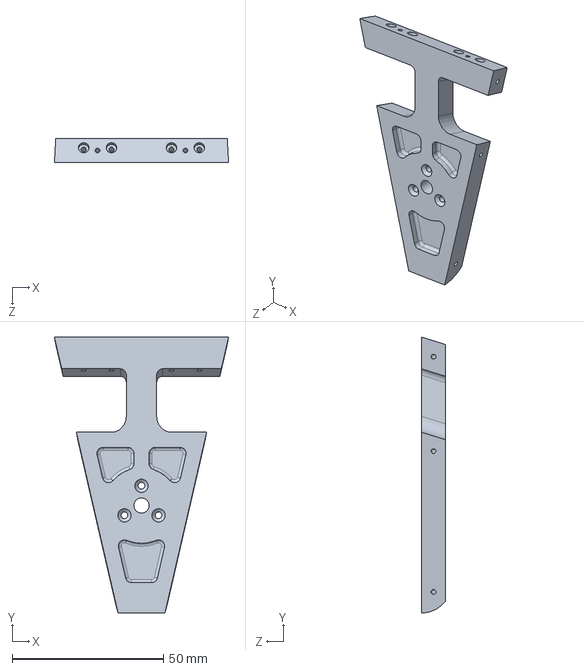
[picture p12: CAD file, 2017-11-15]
model/split_files/roll_motor_mount.sldprt
57.5 x 91.1 x 8.00 mm

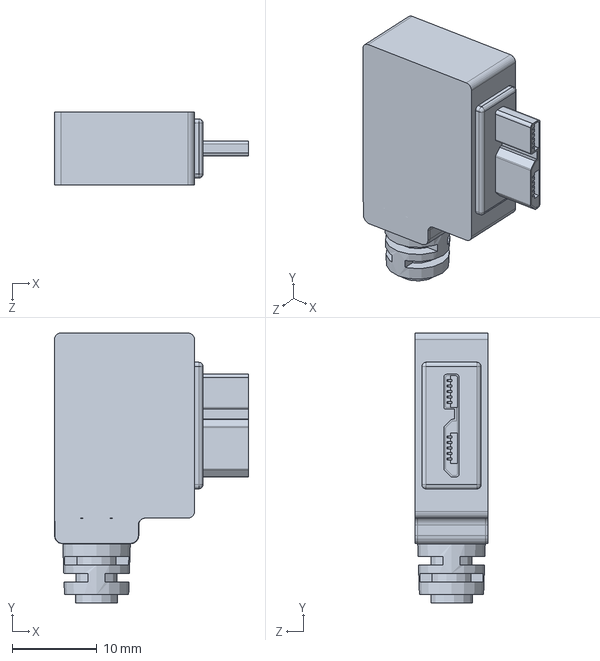
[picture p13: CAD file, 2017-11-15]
model/USBFIREWIRE_COM-MCBL3/USBFIREWIRE_COM-MCBL3.SLDPRT
23.0 x 32.0 x 8.64 mm

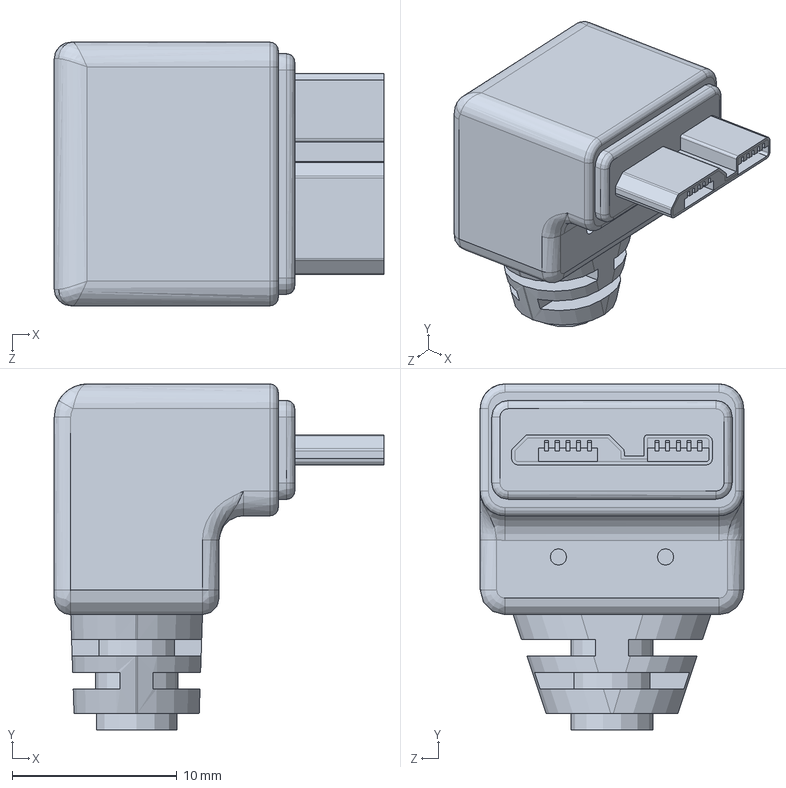
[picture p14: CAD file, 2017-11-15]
model/USBFIREWIRE_COM-MCBU3/USBFIREWIRE_COM-MCBU3.SLDPRT
20.0 x 21.0 x 16.0 mm

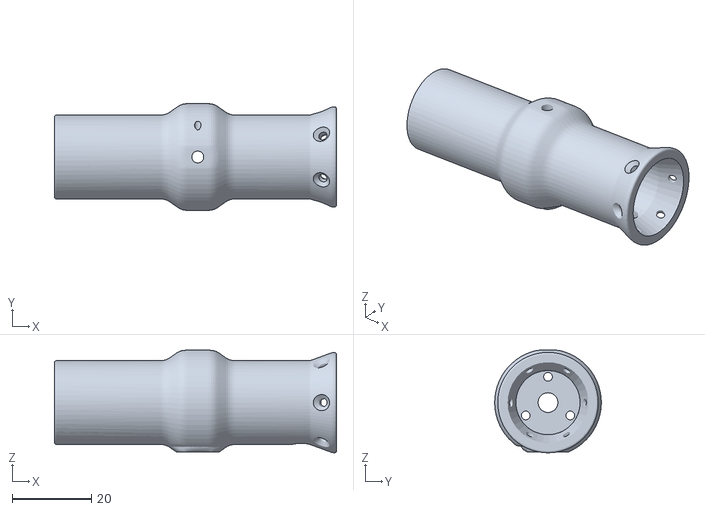
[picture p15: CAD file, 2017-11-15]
model/2016_07_13_MFG_RELEASE/pitch_link.STL
71.3 x 27.0 x 25.9

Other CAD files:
model/estop/A22E_S_01.SLDASM
model/estop/A22_02M.SLDASM
model/maxon16dxl/maxon_PN_B75AECFD27A3_8_2.sldprt
model/USBFIREWIRE_COM-MCBR3/USBFIREWIRE_COM-MCBR3.SLDPRT
model/1.sldprt
model/2.sldprt
model/2016_07_13_MFG_RELEASE/dogbone_link2.STL
model/2016_07_13_MFG_RELEASE/pitch_link.SLDDRW
model/2016_07_13_MFG_RELEASE/pitch_link_end_cap.STL
model/2016_07_13_MFG_RELEASE/vesa_flange.SLDDRW
model/2016_07_13_MFG_RELEASE/yaw_link.SLDDRW
model/2016_07_13_MFG_RELEASE/yaw_shaft.SLDDRW
model/2016_07_13_MFG_RELEASE/yoke.SLDDRW
model/2016_07_13_MFG_RELEASE/yoke.STL
model/24337_Keystone.SLDPRT
model/3.sldprt
model/3088A119.SLDPRT
model/3088A124.SLDPRT
model/3088A229.SLDPRT
model/4262T360.SLDPRT
model/4262T500.SLDPRT
model/6680K110.SLDPRT
model/90318A101.SLDPRT
model/90318A102.SLDPRT
model/90337A197.SLDPRT
model/91239A140.SLDPRT
model/91239A758.SLDPRT
model/91255A075.SLDPRT
model/91292A265.SLDPRT
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

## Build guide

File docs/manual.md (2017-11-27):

# OREO Manual 
This is a work-in-progress manual that covers setup and basic use of the OREO robot. Unfortunately, it is based on notes that were taken after the robot was complete, during the process of setting up the robot on a new computer. So it is missing some procedures that were performed during the initial robot setup. We will expand it the next time the robot is configured from scratch. 

## System Overview
The head has seven degrees of freedom: yaw, pitch, and roll in the neck, and yaw and pitch in each eye. Position in each degree of freedom is sensed by a rotary encoder. The neck is moved by rotary motors. The controllers for these motors are in the base. The eyes are moved by linear actuators, and their controller is on top of the head. Calibration is needed to map the linear actuator positions to the eye angles. 

The main hardware components of the system are: 
* 7-DOF gimbal (Consists of motors, encoders, controllers, frame, linkages, and cabling. Manufacture and assembly are not covered here.)
* Cameras (Point Grey Flea3 FL3-U3-13S2C-CS)
* Fixed lenses (Edmund Optics 58-000 - 8.5mm Compact Fixed Focal Length Lens)
* Variable-focus lenses (-600 to 160FL, VIS, Optotune Industrial Focus-Tunable Lens) 
* Ethernet switch
* A host computer with a Windows OS. 

The following software is needed on the host computer: 
* FLIR Spinnaker (the camera SDK)
* Matlab
* Custom Matlab scripts (in the matlab repository folder)
* Technosoft EasyMotion Studio
* MinGW (includes gcc)
* Optotune software

### Motor Controllers 
Review the manuals (available online) for EasyMotion studio, language, and setup. Searching with google site:technosoft.com is more effective than help.

Note: 
* EasyMotion Studio has a command interpreter that you can use to send commands over Ethernet to controllers. 
* EasyMotion Studio has a Binary Code Viewer that shows binary versions of commands (these are the . This is what must be send from Matlab etc. to get values and set controller to run code at a certain address. 

The linear actuators have Hall encoders. These are incremental (relative to position at startup). Feedback control of eye positions runs on the controller cards and is based on the linear Hall encoders only (not the rotary encoders). 

The neck uses rotary encoders for PID feedback. 

## Setup
### Software Installation
Install Technosoft EasyMotion Studio by running ESM_installer.exe. The download at technosoftmotion.com is a demo that doesn’t support Ethernet communication. You must register to get a functional copy. 

Copy and unzip “EMS Projects/Eye Drive May 16 2017” and “EMS Projects/Eye Drive May 16 2017” to Program Files  (x86) / Technosoft  /ESM / Projects

Install Matlab. 

Try to run calibration.m. This may prompt installation of a Matlab-MinGW adapter, which you can do from the AddOns menu. If this process does not result in MinGW being installed properly, install MinGW manually (see below) and try again. 

If MinGW didn’t install from Matlab, install 64-bit MinGW (includes gcc; make sure gcc stuff included) on host computer. There are multiple versions of MinGW on the internet and not all of them will work. This is the one: https://sourceforge.net/projects/tdm-gcc/files/TDM-GCC%20Installer/Previous/1.1309.0/tdm64-gcc-4.9.2.exe/download Add C:\MinGW\bin to Path environment variable (in Advanced System Settings from right-click-Start->System). 

Build DLL using command in README file if Matlab hasn’t done it. 

Install FLIR Spinnaker for the cameras. This should be independent of the above steps, but doing it first seems to prevent EasyMotion studio from installing properly. This is a download from the Point Grey web site. Select “Application Development” during the installation and install the default components. Launch SpinView, plug in the cameras, and see if they work. 

### Hardware
Clamp robot to a stable base. 
Connect both controllers (top of head and within base) to Ethernet switch, connect computer Ethernet to switch, set subnet of that Ethernet card to 192.168.2, IP to 192.168.2.2, default gateway 192.168.2.1.
Open EasyMotion studio, choose axis, communication->setup, make the port right. It should say “online” in green at bottom of EasyMotion window. If not, try pinging control boards (eye controller is 192.168.2.14 and neck controller is 192.168.2.15). 


Check communication with command interpreter, e.g. “?apos2” should return encoder position for axis 2. 

## Procedures 
### Startup 
Move robot to neutral position. 
Make sure wires are not hung up on anything. 
Run calibration.m. 
You can now run other code. 

### Calibration
Calibration maps desired eye angles to corresponding linear encoder positions. This is used to give feedforward commands. 

Run calibration.m every time robot starts up. This moves the eye actuators through their range of motion while reading encoder values, and then performs a least-squares fit of the motor-angle model parameters. This must be done every time power is cycled, because there is no absolute reference for the motor positions; they are relative to their positions at startup. First make sure eyes are roughly centred to begin (move and hold the eyes manually by holding the cameras’ USB3 cables). Note this procedure will stop if current is unexpectedly high (which is conservative, in case a wire gets hung up). 

### Test Encoders 
In EMS, drive setup. Select test connections. 

### Shutdown
Hold robot by the eyebrows so it doesn’t fall when neck pitch torque turns off. Turn the power off. 

### Setting Max Speed
TODO 

### Controller Tuning on Drives
TODO 
Note: this procedure can reset the drives and move the robot quickly, so have hand on power and be ready to catch chin. 

### Network
Everything is on 2 subnet. Eye controller is 192.168.2.14 and neck is 192.168.2.15. Eye host ID is 120, and neck is 121 (these are Ethernet to canbus adapters; called Axis ID in UI). These are used in communication setup in EasyMotion studio. Each axis has an axis ID additionally. In the neck, 1, 2, 3 are yaw, pitch, roll. Ordered from right to left motor for eyes. One eye encoder is plugged into each drive, in order yaw, pitch, pitch, yaw. So if you want to read from right eye yaw encoder, you must talk to axis one. 

### Updating Parameters on Control Cards
The three neck axes have very different controller gains. Particularly the pitch gain is much higher. 
To reset, open neck project in EasyMotion Studio. Select an axis, select large Edit icon in setup screen, check parameters (use Motor Setup and Drive Setup buttons to get to all the parameters), click OK. 
To program controller, click “Download to drive/motor” for each axis to get control params on controller, also go into “motion” and click run to get code on controller. Axis number is under “application general information”. Axis numbers can be set programmatically but are currently set to “use hardware”. This means they are configured with jumpers on the card (see card manual). These are currently set so the axes are in order starting at the Ethernet-CAN adapter side.

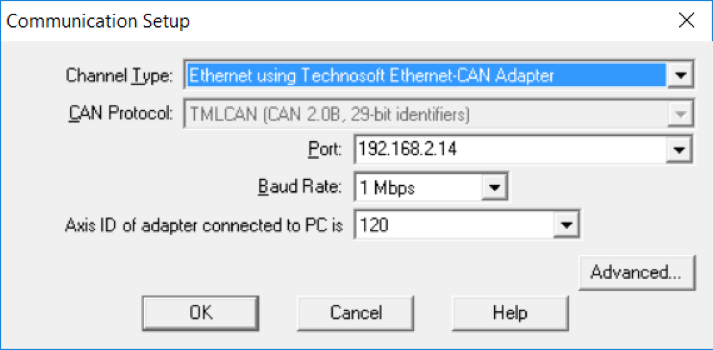
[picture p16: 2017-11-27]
docs/images/em-comm-setup.png

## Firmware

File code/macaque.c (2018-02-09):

#include <winsock2.h>
#include <windows.h>
#include <stdio.h>
#include <stdint.h>
#include <math.h>
#include "macaque.h"

#define COUNTS_PER_POLE	((double)2048)
#define METERS_PER_POLE ((double)0.018)
#define IU_TO_M (METERS_PER_POLE/COUNTS_PER_POLE)
#define M_TO_IU (COUNTS_PER_POLE/METERS_PER_POLE)
#define COUNTS_PER_REV 	((double)5000)
#define COUNTS_PER_REV_YAW 	((double)16*86)
#define IU_TO_RAD (M_PI/(2*COUNTS_PER_REV))
#define RAD_TO_IU (1/IU_TO_RAD)
#define IU_TO_RAD_YAW (M_PI/(2*COUNTS_PER_REV_YAW))
#define RAD_TO_IU_YAW (1/IU_TO_RAD_YAW)

#define SAMPLE_PERIOD_EYE_S	0.0005
#define SAMPLE_PERIOD_NECK_S	0.001
	
#define MPSS_TO_ACCEL_IU		(SAMPLE_PERIOD_EYE_S * SAMPLE_PERIOD_EYE_S * M_TO_IU)
#define ACCEL_IU_TO_MPSS		(1.0 / MPSS_TO_ACCEL_IU)
#define MPS_TO_SPEED_IU		        (SAMPLE_PERIOD_EYE_S * M_TO_IU)
#define SPEED_IU_TO_MPS		        (1.0 / MPS_TO_SPEED_IU)

#define RADPSS_TO_ACCEL_IU		(SAMPLE_PERIOD_NECK_S * SAMPLE_PERIOD_NECK_S * RAD_TO_IU)
#define RADPSS_TO_ACCEL_IU_YAW	(SAMPLE_PERIOD_NECK_S * SAMPLE_PERIOD_NECK_S * RAD_TO_IU_YAW)
#define ACCEL_IU_TO_RADPSS		(1.0 / RADPSS_TO_ACCEL_IU)
#define RADPS_TO_SPEED_IU		(SAMPLE_PERIOD_NECK_S * RAD_TO_IU)
#define RADPS_TO_SPEED_IU_YAW    (SAMPLE_PERIOD_NECK_S * RAD_TO_IU_YAW)
#define SPEED_IU_TO_RADPS		(1.0 / RADPS_TO_SPEED_IU)

#define GETBYTES_FROM_WORD(src,dst_p) (*(uint16_t*)(dst_p) = htons((uint16_t)src))
#define GETBYTES_FROM_LONG(src,dst_p) (*(uint32_t*)(dst_p) = htonl((uint32_t)src))
#define GETWORD_FROM_BYTES(src_p) (ntohs(*(uint16_t*)(src_p)))
#define GETLONG_FROM_BYTES(src_p) (ntohs((*(uint32_t*)src_p)&0xFFFF) | (ntohs((*(uint32_t*)src_p)>>16)<<16))

BOOL ErrorHandler( DWORD fdwCtrlType ) 
{ 

  cleanup();
  
  switch( fdwCtrlType ) 
  { 
    // Handle the CTRL-C signal. 
    case CTRL_C_EVENT: 
      printf( "Ctrl-C event\n\n" );
      Beep( 750, 300 ); 
      return( TRUE );
 
    // CTRL-CLOSE: confirm that the user wants to exit. 
    case CTRL_CLOSE_EVENT: 
      Beep( 600, 200 ); 
      printf( "Ctrl-Close event\n\n" );
      return( TRUE ); 
 
    // Pass other signals to the next handler. 
    case CTRL_BREAK_EVENT: 
      Beep( 900, 200 ); 
      printf( "Ctrl-Break event\n\n" );
      return FALSE; 
 
    case CTRL_LOGOFF_EVENT: 
      Beep( 1000, 200 ); 
      printf( "Ctrl-Logoff event\n\n" );
      return FALSE; 
 
    case CTRL_SHUTDOWN_EVENT: 
      Beep( 750, 500 ); 
      printf( "Ctrl-Shutdown event\n\n" );
      return FALSE; 
 
    default: 
      return FALSE; 
  } 
} 

double convert_iu_to_m(int32_t iu)
{
    return IU_TO_M * iu;
}

int32_t convert_m_to_iu(double m)
{
    return (int32_t)(M_TO_IU * m);
}

double convert_iu_to_rad(int32_t iu)
{
    return IU_TO_RAD * iu;
}

double convert_iu_to_rad_yaw(int32_t iu)
{
    return IU_TO_RAD_YAW * iu;
}

typedef struct rawData
{
    uint8_t id;
    double data;
    double time;
} rawData_t;

typedef struct rawDataLog
{
    uint32_t		index;
    rawData_t           entry[LOG_BUFLEN];
} rawDataLog_t;

typedef struct msg
{
    uint8_t msg[BUFLEN];
    int  size;
} msg_t;

static WSADATA wsa;

static eyeData_t eyeData;
static eyeCalData_t eyeCalData;
static rawDataLog_t eyeLogData;

static neckData_t neckData;
static rawDataLog_t neckLogData;

typedef void(*rxCallbackFxn)(uint16_t, uint16_t, int32_t);
void eyeRxCallback(uint16_t axis_id, uint16_t reg_addr, int32_t data);
void neckRxCallback(uint16_t axis_id, uint16_t reg_addr, int32_t data);
static double get_timestamp();

typedef struct devHandle
{
    SOCKET             	sock;
    struct sockaddr_in 	addr;
    int                	addr_len;

    const int          	local_port;
    const char* const  	ip;
    
    int         	runFlag;
    HANDLE      	txThreadHandle;
    HANDLE      	rxThreadHandle;
    char        	rx_buf[BUFLEN];

    uint32_t         	ack_pend;
    uint8_t		force_sync;

    msg_t		cmd_buf[MAX_CMD_PEND];
    uint32_t		cmd_consume_idx;
    uint32_t		cmd_produce_idx;
    uint8_t		host_id;

    rxCallbackFxn	callback;

} devHandle_t;

devHandle_t eye  = {.local_port = EYE_LOCAL_PORT, .ip = EYE_IP, .force_sync=0,
                    .ack_pend = 0, .cmd_consume_idx = 0, .cmd_produce_idx = 0, 
		    .host_id = EYE_HOST_ID, .callback = &eyeRxCallback};

devHandle_t neck = {.local_port = NECK_LOCAL_PORT, .ip = NECK_IP, .force_sync=0,
                    .ack_pend = 0, .cmd_consume_idx = 0, .cmd_produce_idx = 0, 
		    .host_id = NECK_HOST_ID, .callback = &neckRxCallback};

static void add_log_data(rawDataLog_t* log, double time, double data, uint8_t id)
{
    log->entry[log->index].data = data;
    log->entry[log->index].time = time;
    log->entry[log->index].id   = id;
    log->index = (++log->index < LOG_BUFLEN)?log->index:0;	 
}

void neckRxCallback(uint16_t axis_id, uint16_t reg_addr, int32_t data)
{
    neckData.time = get_timestamp();
    double converted_data;
    uint8_t log_data_id;

    switch (reg_addr)
    {
        case REG_ADDR_APOS & REG_ADDR_MASK:
            converted_data = convert_iu_to_rad(data);
            break;
        default:
            break;
    }

    switch (axis_id)
    {
        case NECK_YAW_AXIS:
            log_data_id = NECK_YAW; 
            neckData.yaw = convert_iu_to_rad_yaw(data);
            break;
        case NECK_PITCH_AXIS:
            log_data_id = NECK_PITCH;
	    neckData.pitch = converted_data;
            break;
        case NECK_ROLL_AXIS:
            log_data_id = NECK_ROLL;
	    neckData.roll = converted_data;
            break;
        default:
            break;
    }

    add_log_data(&neckLogData, neckData.time, converted_data, log_data_id);
}

void eyeRxCallback(uint16_t axis_id, uint16_t reg_addr, int32_t data)
{

    double converted_data;
    uint8_t log_data_id;
    double time = get_timestamp();
    switch (reg_addr)
    {
        case REG_ADDR_APOS & REG_ADDR_MASK:
            log_data_id = 1;
            converted_data = convert_iu_to_m(data);
            eyeCalData.time = time;
            eyeCalData.pos[axis_id-1] = converted_data;
            break;

        case REG_ADDR_POSERR & REG_ADDR_MASK:
            log_data_id = 2;
            converted_data = convert_iu_to_m(data);
            eyeCalData.time = time;
            eyeCalData.err[axis_id-1] = converted_data;
            break;

        case REG_ADDR_TPOS & REG_ADDR_MASK:
            log_data_id = 3;
            converted_data = convert_iu_to_m(data);
            eyeCalData.time = time;
            eyeCalData.tpos[axis_id-1] = converted_data;
            break;

        case REG_ADDR_APOS2 & REG_ADDR_MASK:
            log_data_id = 0;
            eyeData.time = time;
            converted_data = convert_iu_to_rad(data);

            switch (axis_id)
            {
                case EYE_YAW_LEFT_AXIS:
                    eyeData.yaw[LEFT] = converted_data;
                    break;
                case EYE_YAW_RIGHT_AXIS:
                    eyeData.yaw[RIGHT] = converted_data;
                    break;
                case EYE_PITCH_LEFT_AXIS:
                    eyeData.pitch[LEFT] = converted_data;
                    break;
                case EYE_PITCH_RIGHT_AXIS:
                    eyeData.pitch[RIGHT] = converted_data;
                    break;
                default:
                    break;
            }
            
            break;

        case CAL_RUN_VAR & REG_ADDR_MASK:
            eyeCalData.complete[axis_id-1] = data;
            break;

	    case CAL_APOS2_OFF_VAR & REG_ADDR_MASK:
            eyeData.time = time;
            converted_data = convert_iu_to_rad(data);

            switch (axis_id)
            {
                case EYE_YAW_LEFT_AXIS:
                    eyeData.yaw_offset[LEFT] = converted_data;
                    break;
                case EYE_YAW_RIGHT_AXIS:
                    eyeData.yaw_offset[RIGHT] = converted_data;
                    break;
                case EYE_PITCH_LEFT_AXIS:
                    eyeData.pitch_offset[LEFT] = converted_data;
                    break;
                case EYE_PITCH_RIGHT_AXIS:
                    eyeData.pitch_offset[RIGHT] = converted_data;
                    break;
                default:
                    break;
            }
	    break;

        default:
            break;
    }

    add_log_data(&eyeLogData, time, converted_data, (log_data_id*NUM_EYE_AXIS)+axis_id-1);
}

static uint8_t gen_cksum(uint8_t *msg, uint8_t size)
{
    uint8_t cksum=0;
    uint8_t n=0;
    for(n=0; n < size-1; n++)
    {
        cksum+=msg[n];
    }

    return cksum&0xFF;
}

static uint16_t build_addr(uint8_t axis_id, uint8_t is_host, uint8_t is_group)
{
    uint16_t addr;
    addr = (axis_id&0xFF) << 4;
    addr |= (is_host)?0x0001:0x0000;
    addr |= (is_group)?0x1000:0x0000;
    return addr;
}

static uint8_t get_addr(uint16_t formatted)
{
    uint8_t addr;
    addr = (uint8_t)((formatted&0x0FF0) >> 4);
    return addr;
}

static void parse_response_msg(devHandle_t* dev)
{   
    uint8_t *msg = dev->rx_buf;
    int32_t result = 0;
    uint16_t axis;
    uint16_t reg_addr;

    if(msg == NULL)
    {  
        return;
    }

    int size = msg[MSG_SIZE_OFFSET]+2;
    
    if( msg[size-1] != gen_cksum(msg,size) || size < MSG_TYPEA_BASE)
    {
        return;
    }

    uint16_t dst_addr   = get_addr(GETWORD_FROM_BYTES(&msg[MSG_ADDR_OFFSET]));
    uint16_t optcode    = GETWORD_FROM_BYTES(&msg[MSG_OPT_OFFSET]);

    if (((optcode&MSG_TAKE_OPTCODE_MASK) == (OPT_1WORD_TAKE&MSG_TAKE_OPTCODE_MASK)) 
        && size == MSG_TAKE1WORD_SIZE)
    {
        axis         = optcode&0xFF;      
        reg_addr     = GETWORD_FROM_BYTES(&msg[MSG_TAKE_REG_ADDR_OFFSET]);
        int16_t temp = GETWORD_FROM_BYTES(&msg[MSG_TAKE_DATA_OFFSET]);
        result       = (int32_t)temp;
    }
    else if (((optcode&MSG_TAKE_OPTCODE_MASK) == (OPT_2WORD_TAKE&MSG_TAKE_OPTCODE_MASK))
             && size == MSG_TAKE2WORD_SIZE)
    {
        axis     = optcode&0xFF;
        reg_addr = GETWORD_FROM_BYTES(&msg[MSG_TAKE_REG_ADDR_OFFSET]);	
        result   = GETLONG_FROM_BYTES(&msg[MSG_TAKE_DATA_OFFSET]);
    }	
    else if(optcode == OPT_1WORD_RESP && size == MSG_GIVE1WORD_SIZE)
    {
        axis         = get_addr(GETWORD_FROM_BYTES(&msg[MSG_SEND_ADDR_OFFSET]));
        reg_addr     = GETWORD_FROM_BYTES(&msg[MSG_GIVE_REG_ADDR_OFFSET]);
        int16_t temp = GETWORD_FROM_BYTES(&msg[MSG_GIVE_DATA_OFFSET]);
        result       = (int32_t)temp;
    }
    else if(optcode == OPT_2WORD_RESP && size == MSG_GIVE2WORD_SIZE)
    { 
        axis       = get_addr(GETWORD_FROM_BYTES(&msg[MSG_SEND_ADDR_OFFSET]));
        reg_addr   = GETWORD_FROM_BYTES(&msg[MSG_GIVE_REG_ADDR_OFFSET]);
        result     = GETLONG_FROM_BYTES(&msg[MSG_GIVE_DATA_OFFSET]);
    }

    if(dev->callback!=NULL)
        dev->callback(axis, reg_addr, result);
}

static uint64_t timebase;

static double get_timestamp()
{
    FILETIME tm;
    uint64_t t;
    GetSystemTimePreciseAsFileTime(&tm);
    t = ((uint64_t)tm.dwHighDateTime << 32) | (uint64_t)tm.dwLowDateTime;
    t = t - timebase;
    return (double)t / 10000000.0;
}
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

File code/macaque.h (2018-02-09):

#include <stdint.h>

#define SHUTDOWN_TIMEOUT_MS 	2000
#define RX_TIMEOUT_MS		1000
#define SEND_TIMEOUT_S		1.0
#define BUFLEN 			32  	
#define LOG_BUFLEN		1024
#define MAX_ACK_PEND 		4  //limit how much we pound the drives with polls for data
#define MAX_CMD_PEND 		8  //must be a power of 2

#define CONN_PORT		30689u
#define CONN_MSG		((uint8_t[]){0x01})
#define CONN_RESP		((uint8_t)0x02)
#define CONN_CONFIG	        ((uint8_t[]){0x03,0x00,0xC2,0x01,0x00})//1Mbit config
#define CONN_CONFIG_RESP	((uint8_t)0x04)
#define CONN_ERR		1
#define CONN_CONFIG_ERR		2
#define CONN_SYNC_ERR		3
#define CONN_OK			0
#define CONN_SYNC_RESP		0x0Du
#define CONN_SYNC_BYTES		15
#define CONN_SYNC_BYTE		0xFFu
#define DISCONN_MSG		((uint8_t[]){0x05})
#define DISCONN_RESP		((uint8_t)0x06)

#define COMM_PORT		1700
#define MSG_ACK			((uint8_t)0x4F)

#define NECK_HOST_ID		121
#define NECK_LOCAL_PORT		51244u
#define NECK_IP			"192.168.2.15"

#define EYE_HOST_ID		120
#define EYE_LOCAL_PORT		51243u
#define EYE_IP			"192.168.2.14"

#define MSG_TYPEA_BASE		6
#define MSG_TYPEB_BASE		10
#define MSG_SIZE_OFFSET		0
#define MSG_ADDR_OFFSET		1
#define MSG_OPT_OFFSET		3
#define MSG_SEND_ADDR_OFFSET	5
#define MSG_TAKE_REG_ADDR_OFFSET 5
#define MSG_GIVE_REG_ADDR_OFFSET 7
#define MSG_TAKE_DATA_OFFSET	7
#define MSG_GIVE_DATA_OFFSET	9
#define MSG_TAKE1WORD_SIZE	10
#define MSG_TAKE2WORD_SIZE	12
#define MSG_GIVE1WORD_SIZE	12
#define MSG_GIVE2WORD_SIZE	14
#define MSG_TAKE_OPTCODE_MASK   0xFF00

#define OPT_1WORD_RESP		0xB404u
#define OPT_2WORD_RESP		0xB405u
#define OPT_1WORD_TAKE		0xD400u
#define OPT_2WORD_TAKE		0xD500u
#define OPT_1WORD_REQ		0xB004u
#define OPT_2WORD_REQ		0xB005u
#define OPT_CACC		0x24A2u
#define OPT_CSPD		0x24A0u
#define OPT_CPOS		0x249Eu
#define OPT_GOTO		0x7400u
#define REG_ADDR_APOS		0x0228u
#define REG_ADDR_POSERR		0x022Au
#define REG_ADDR_APOS2		0x081Cu
#define REG_ADDR_TPOS		0x02B2u
#define REG_ADDR_MASK		0x07FFu

//technosoft drive program specific addresses
#define MOTION_LOOP_IP		0x4022u
#define WAIT_LOOP_IP		0x401Bu
#define MOTION_LOOP_NECK_IP	0x403Bu
#define WAIT_LOOP_NECK_IP	0x4034u
#define REV_CAL_IP		0x4061u
#define FOR_CAL_IP		0x4027u
#define CAL_RUN_VAR		0x03B3u
#define CAL_APOS2_OFF_VAR	0x03B0u

//eye drive defines
#define LEFT			0
#define RIGHT			1
#define NUM_EYES		2
#define NUM_EYE_AXIS		(2*(NUM_EYES))

//axis id mapping
#define EYE_YAW_LEFT_AXIS	1
#define EYE_PITCH_LEFT_AXIS	2
#define EYE_PITCH_RIGHT_AXIS	3
#define EYE_YAW_RIGHT_AXIS	4

//log data id
#define EYE_YAW_LEFT		0
#define EYE_PITCH_LEFT		1
#define EYE_YAW_RIGHT		2
#define EYE_PITCH_RIGHT		3
#define EYE_LEFT_LEFT_POS	4
#define EYE_LEFT_RIGHT_POS	5
#define EYE_RIGHT_LEFT_POS	6
#define EYE_RIGHT_RIGHT_POS	7
#define EYE_LEFT_LEFT_POSERR	8
#define EYE_LEFT_RIGHT_POSERR 	9
#define EYE_RIGHT_LEFT_POSERR	10
#define EYE_RIGHT_RIGHT_POSERR	11

//neck drive defines
//axis id mapping
#define NUM_NECK_AXIS		3
#define NECK_YAW_AXIS		1
#define NECK_PITCH_AXIS		2
#define NECK_ROLL_AXIS		3

//log data id
#define NECK_YAW		0
#define NECK_PITCH		1
#define NECK_ROLL		2

#define CAL_COMPLETE		0
#define CAL_RUNNING		1

typedef struct eyeCalData
{
    double time;
    double pos[NUM_EYE_AXIS];
    double err[NUM_EYE_AXIS];
    double tpos[NUM_EYE_AXIS];
    uint16_t complete[NUM_EYE_AXIS];
} eyeCalData_t;

typedef struct eyeData
{
    double yaw[NUM_EYES];
    double yaw_offset[NUM_EYES];
    double pitch[NUM_EYES];
    double pitch_offset[NUM_EYES];
    double time;
} eyeData_t;

typedef struct neckData
{
    double yaw;
    double pitch;
    double roll;
    double time;
} neckData_t;

void sendMsgTypeAEye(uint8_t axis_id, uint16_t optcode, uint32_t data, uint8_t words, uint8_t group);

void sendMsgTypeBEye(uint8_t axis_id, uint16_t reg_addr, uint8_t words);

void sendMsgTypeANeck(uint8_t axis_id, uint16_t optcode, uint32_t data, uint8_t words, uint8_t group);

void sendMsgTypeBNeck(uint8_t axis_id, uint16_t reg_addr, uint8_t words);
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

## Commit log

2018-02-06 adding calibration based on EyeGeometry class
2018-02-09 updates for new yaw motor; note there is a problem that seems to require a 1/2s pause before issuing neck commands
2018-02-09 updating left eye to use EyeGeometry calibration; adding pauses to reduce apparent network congestion
2018-10-09 new optional visual correction of calibration
